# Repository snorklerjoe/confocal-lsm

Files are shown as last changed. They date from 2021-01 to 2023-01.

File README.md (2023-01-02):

# confocal-lsm
Hardware and software for my homemade **laser-scanning confocal microscope**

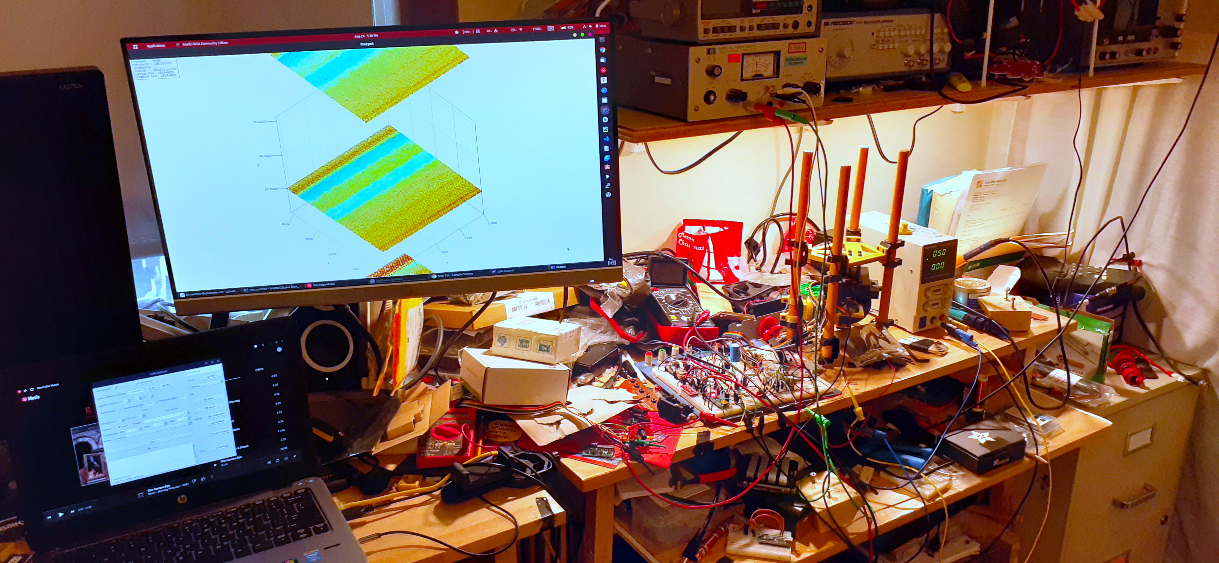
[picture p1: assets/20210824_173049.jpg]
My desk during development


_My desk during development_

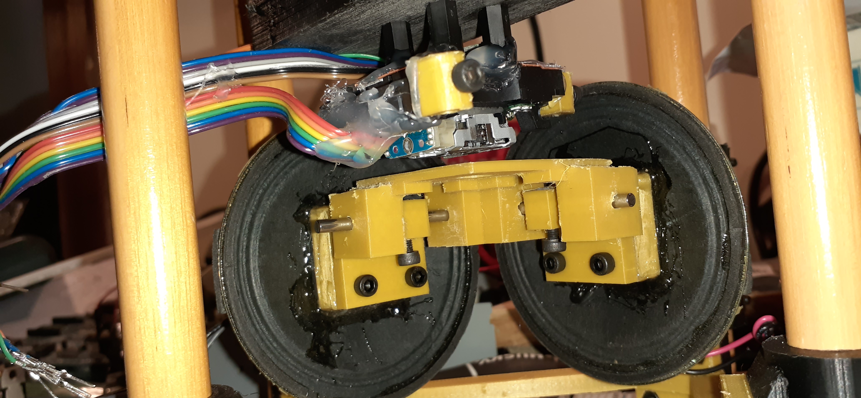
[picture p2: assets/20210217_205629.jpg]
The Scanning Mechanism


_A close-up of the scanning stage and optical head_

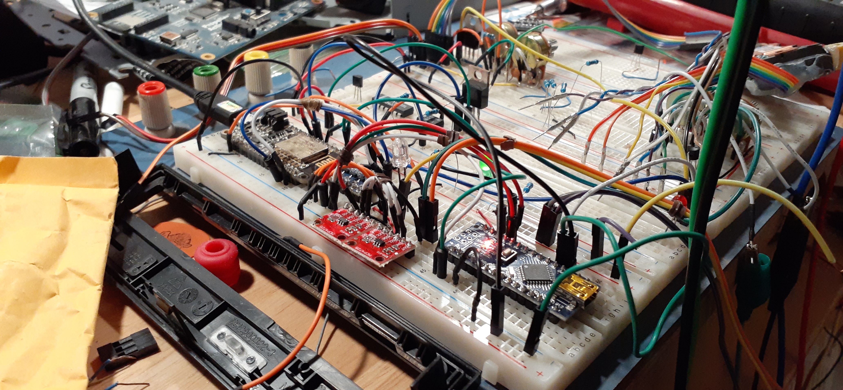
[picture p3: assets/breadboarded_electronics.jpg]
A picture of the breadboarded electronics


_Breadboarded control electronics_

## Origins...
After reading [this Instructables](https://www.instructables.com/id/Laser-Scanning-Microscope/) and [this Hackaday article](https://hackaday.com/2017/02/15/speakers-make-a-laser-scanning-microscope/),
I thought it would be interesting to try my hand at building a laser scanning microscope from CD/DVD drive parts...

# Iterative Development:

## V1 (~Summer 2018)
The first iteration scanned the specimen in the x and z axes to change its position relative to a laser beam. The diffused reflection was then measured by a usb camera and recorded into software.

This configuration was not confocal, and could only measure the X-Z plane, but was rather intended as a proof-of-concept test in which I began to learn how to explore this topic deeper.

This first "successful" scan is _most likely_ the product of the laser being brightest with the electromagnetic actuators (taken from the tracking assembly of a CD drive head) most centered (drawing the least current) due to resistance in power distribution:

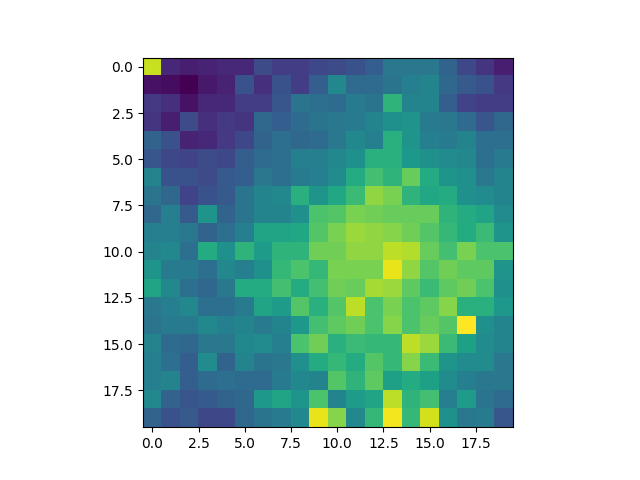
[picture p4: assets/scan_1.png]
scan 1


## V2
The second iteration was the first iteration to be confocal. I used a microscope slide as a beam splitter, with the laser going through a lens moved by the CD drive actuators and a speaker to achieve a third axis of motion. The reflected light was measured by a photoresistor, which proved to have too high of a latency for large scans to be practical.

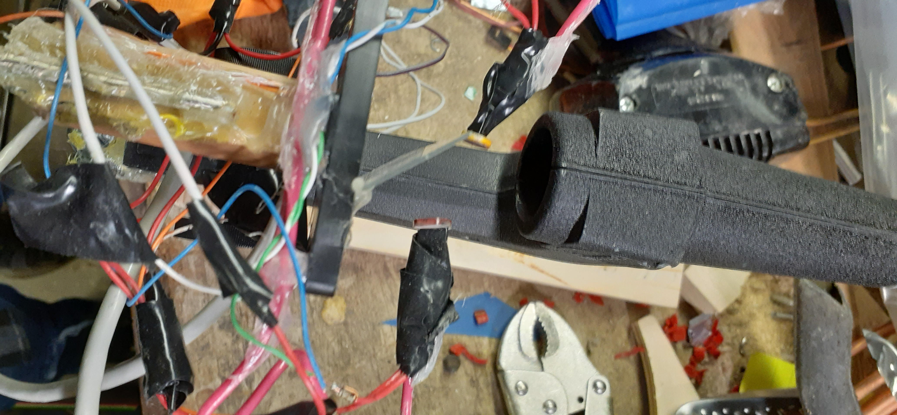
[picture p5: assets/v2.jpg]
The optical layout of prototype 2


Ultimately, due to issues of optical beam quality, the laser could not be focused to a small-enough point to be able to draw conclusions from any results of this revision.

I experimented with different lasers in this iteration in an effort to avoid this problem, using a CD laser and a laser diode from a common laser pointer.

In doing this, I also experimented with a number of simple laser driver circuits (current-limited supplies)

## V3 (2020)
The third iteration rehashed the idea of using a speaker as an actuator, but used a USB camera again as a sensor. I repurposed a desktop PC case and power supply for this iteration to provide a rigid mounting system and reduce current limitation issues.

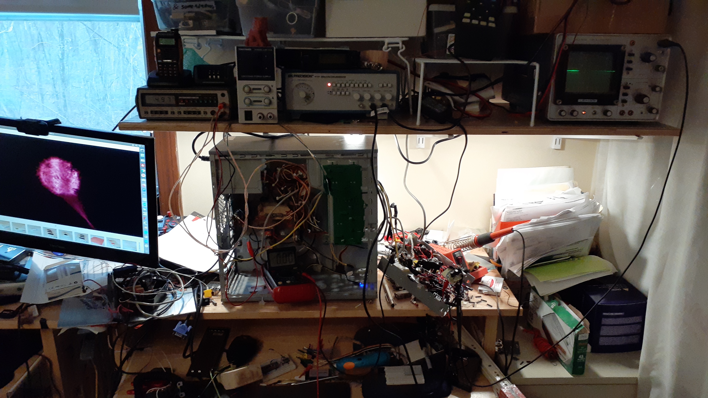
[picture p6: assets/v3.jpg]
An image of my desk with V3


_Testing for independence of laser intensity and actuator current draw (good power distribution)_

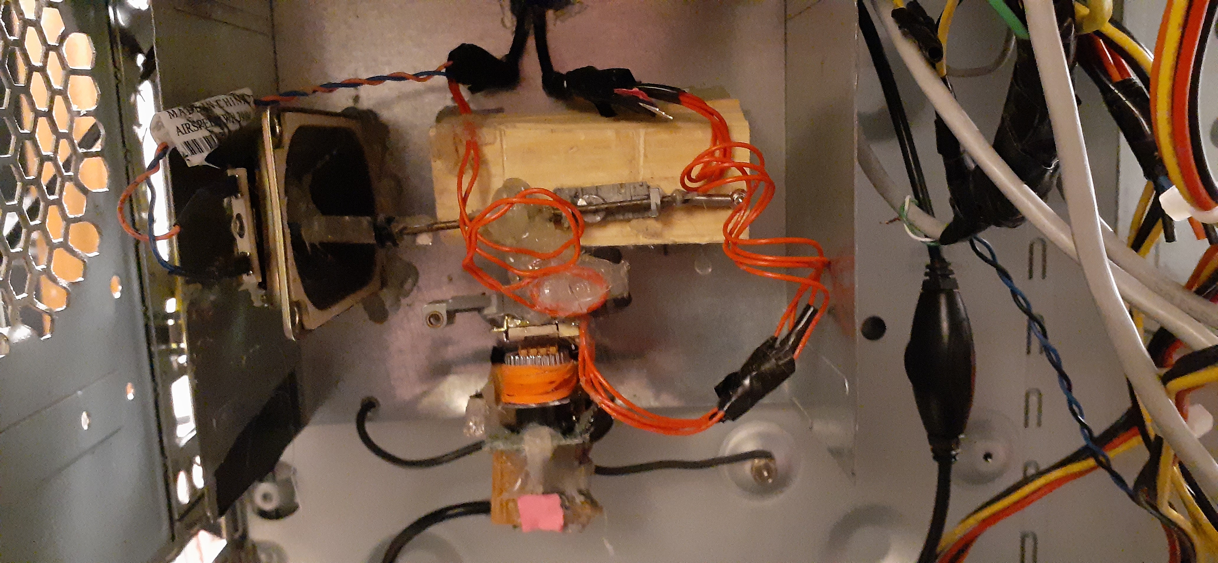
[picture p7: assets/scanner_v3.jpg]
The actuators & scanning mechanism!


_Closeup of the scanning mechamism_

This iteration also involved completely rewriting the software- I created a graphical user interface with PyQT4 and rewrote the image processing to obtain more accurate intensity measurements from the USB camera:

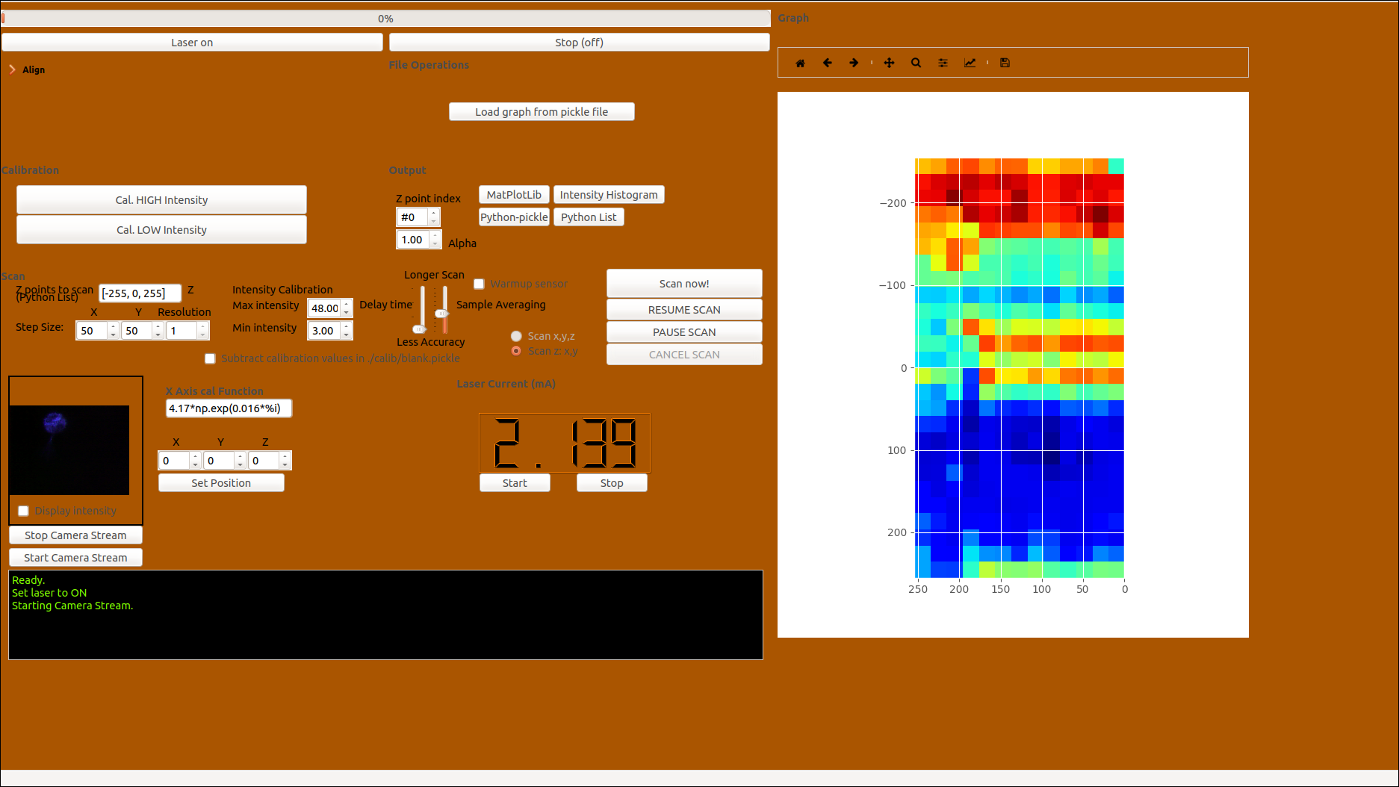
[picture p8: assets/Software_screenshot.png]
Software Screenshot


_A screenshot of the GUI_

I did manage to get a few reasonable images from this iteration of the microscope, the best one being the following:

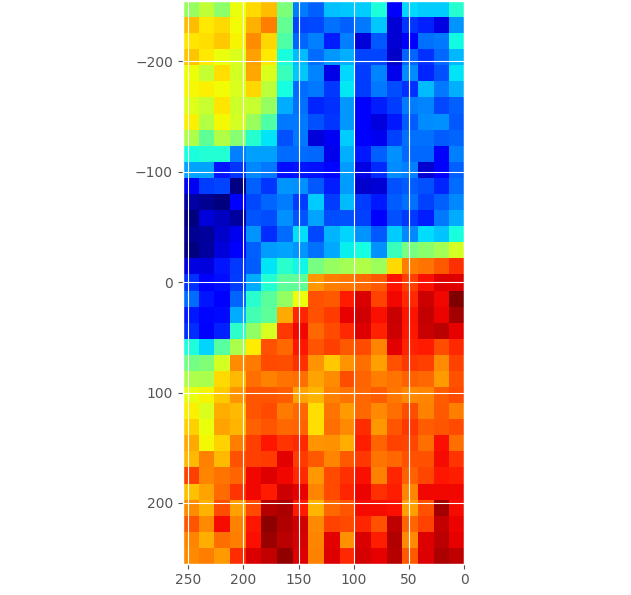
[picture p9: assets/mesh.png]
A Scan


_A scan of the mesh from a speaker grille from a handheld radio_

## V4 (2021-Current)
### Using a Photodiode...
For this iteration, I decided to further investigate how to measure the intensity of transmitted and/or reflected light.
I observed the die of a photodiode used in the optical head of the CD drive under a microscope:

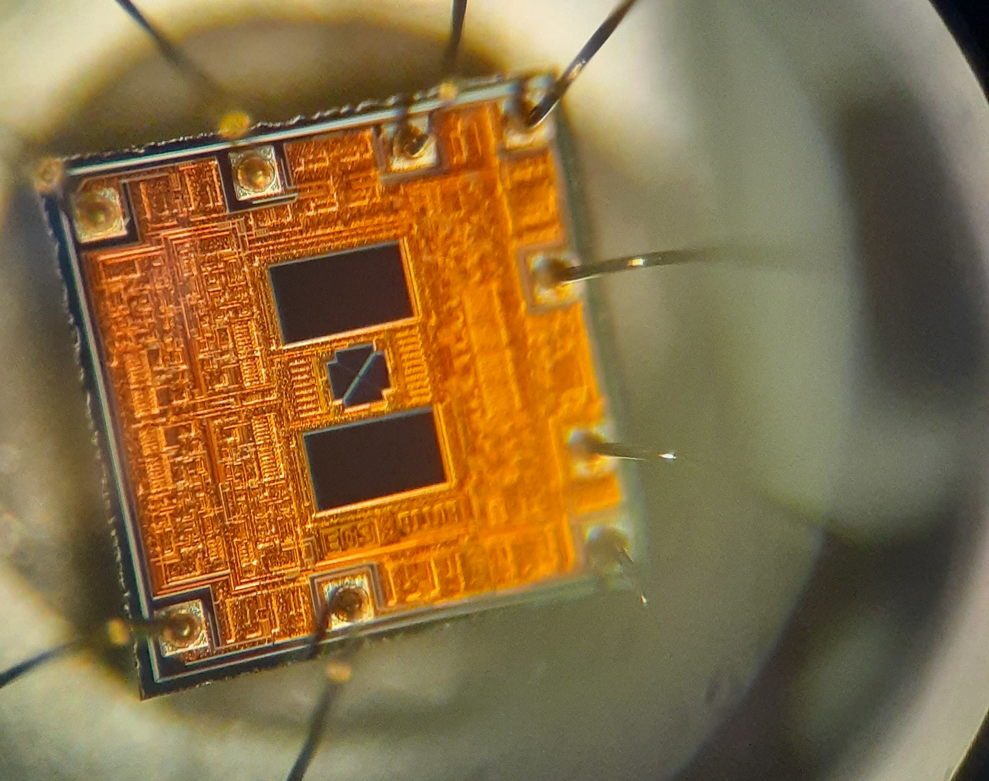
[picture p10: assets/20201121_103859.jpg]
Compound photodiode die under the microscope


It happens that CD drives use a compound photodiode to assist in focusing. After a number of attempts to interface to this photodiode as it was wired into the electronics of the CD drive, I settled upon using a different photodiode instead.

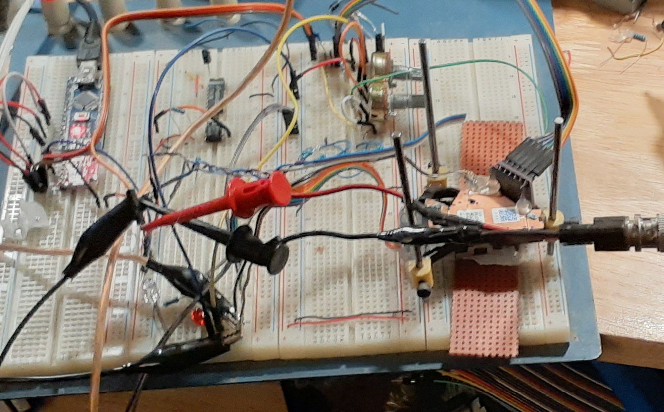
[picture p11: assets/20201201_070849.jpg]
Testing with the new photodiode


### CAD & Redesigned Scanning Mechanism

I then designed a modular frame in FreeCAD, before transfering my design to Fusion360:
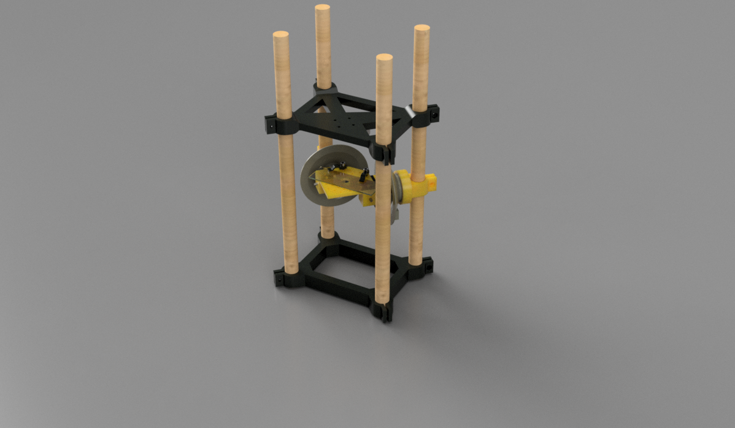
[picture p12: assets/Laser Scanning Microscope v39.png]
A 3D Render


_A Fusion360 Render of the microscope frame_

The Scanning Mechanism

_A close-up of the scanning stage and optical head_

### Electronics

There were also a number of electronic improvements in this iteration- PWM control of the actuators was replaced by 2N2222-based drivers controled by DACs. An LM317 was used to create a constant-current source for the laser diode. Also, the microscope communicates with a computer via the WiFi connection of an ESP8266, with an Arduino Nano being used to handle some of the interfacing tasks over I2C. Overall, this revision represents major improvements in reliability, resolution, and quality.

A picture of the breadboarded electronics

_The electronics on a breadboard_

### Software

The software was rewritten in Java, with a number of improvements, such as...
- Interpreted script-based description of a scanning pattern
- More flexible data aggregation
- More data processing to produce 3-D contour plots of a surface
- Threads to process and recieve data efficiently

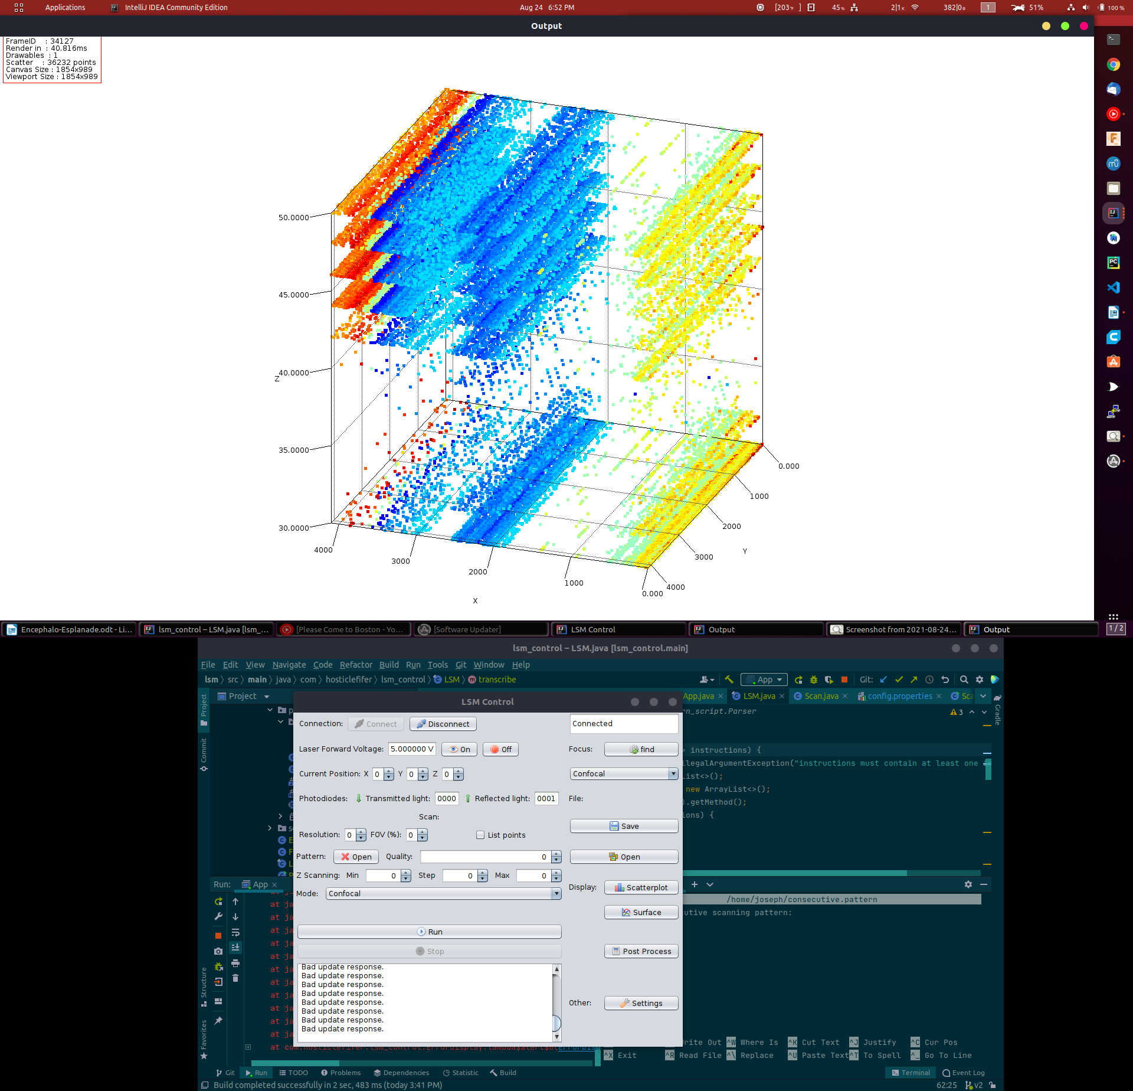
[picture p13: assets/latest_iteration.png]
A Software Screenshot


## Conclusion / Continued Work

I have yet to obtain a scan from this iteration which truly represents the specimen being scanned in an obvious and clear manner, but further work will involve reliability improvements and reducing stiction in the stage to improve precision of the actuators in order to push closer to this goal.

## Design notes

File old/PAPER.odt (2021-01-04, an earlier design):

Building a Transmission-mode Laser Scanning Microscope for Free

Joseph R. Freeston

Department of English, Windham High School

Freshman Writing

June 8, 2020

Abstract

Scientific equipment can often be produced with parts that can be found in old electronics. This paper is intended to inform about how a transmission-mode laser scanning microscope (TLSM) can be constructed for very little monetary cost. A TLSM shines a collimated laser beam into optics which focus it into a small area along the focal plane (which is on the specimen). A TLSM measures the light transmitted through an object, sometimes revealing interesting details about its structure. This reflected light is measured as the beam is scanned along the object in order to capture a grayscale image. Although most laser scanning microscopes are confocal, meaning that the light reflected off of an object goes backward through the objective lens, and is then measured, this one operates only in transmission-mode. This functional piece of equipment is capable of obtaining three-dimensional slices of almost any small, translucent object, and can be built with parts commonly found in old and broken electronics.

Keywords: arduino, laser, microscope, optics

Glossary

1. Actuator
  a. A device that actuates, or moves, something.
2. Beam waist
  a. The diameter of a beam at its focal point (Hinton, 2019).
3. Bipolar Junction Transistor (BJT)
  a. A type of transistor that allows controlling the amount of electric current going from its collector to its emitter by altering the current from its base to its emitter (See “Transistor”).
4. Cadmium-sulfide
  a. A carcinogenic material commonly found in older photoresistors (See “Photoresistor”).
5. Collimation
  a. The process of forming a beam into a straight, column-shaped one by lowering its angle of divergence.
6. Confocal
  a. Meaning that a laser will be focused onto something and in the same manner (through the same optics) be reflected backward to end up in the same place it originated from. The returning beam may also be split off into a detector at the same optical distance from the objective lens as the laser.
7. Current Source
  a. A current source is capable of maintaining a constant current output, even with varying loads, by altering its voltage output.
8. Diaphragm
  a. (In a speaker) The part of a speaker which is actuated back and forth by the coil repelling or attracting a magnet. Normally, the diaphragm turns the mechanical motion into a longitudinal wave going through the air.
9. Duty cycle
  a. The percentage of time that a pulsed signal is in the high or “on” state. If the signal remains high for 90% of the time in between spiking low, it has a 90% duty cycle (See “Pulse-width Modulation”).
10. Electromagnet
  a. A magnet relying on the magnetic field produced around a wire with current flowing through it. These are generally just a coil of wire, often wrapped around a metal core. They may be turned on and off, and even varied, electronically.
11. H-Bridge
  a. An arrangement of transistors that allow reversing the polarity of a device, such as a motor or a coil. They are commonly used to control a motor’s direction.
12. Kirchhoff's Current law
  a. A law that allows multiple devices in series to draw the same amount of current.
13. Microcontroller
  a. A small computer capable of performing calculations and controlling electronics through input/output pins (i/o pins).
14. Ohm
  a. The unit used to measure resistance to the flow of electric current, named after Georg Ohm, the man that discovered Ohm’s Law.
15. Ohm’s Law
  a. The famous equation relating current, voltage, and resistance, stating that V=IR, with “V” being the voltage drop across something, “I” being the current going through it, and “R” being the resistance in ohms (See “Ohm”).
16. Operational Amplifier (Op-Amp)
  a. A device that amplifies a signal based upon the difference between its two inputs.
17. Photodiode
  a. A device that can be used to measure the intensity of light.
18. Photoresistor
  a. Similar to a photodiode, but with a much slower reaction time. It is essentially a resistor whose resistance changes based on light intensity (See “Resistor”).
19. Power supply
  a. A device which usually supplies (a) specific voltage(s) to an electronic circuit, generally converting the high voltage alternating current from an electrical outlet into low-voltage direct current.
20. Pulse-width Modulation (PWM)
  a. A method of synthesizing a nearly analog signal from a digital one by pulsing something and adjusting the duty cycle (See “Duty Cycle”).
21. Resistor
  a. An electronic component that resists the flow of electric current.
22. Speaker
  a. A device that transforms an analog (or almost analog) electrical signal into motion, used to create sound (but used only as an actuator in this project).
23. Transistor
  a. An electronic component which acts as an electronically controlled switch, controlling the flow of electricity with another electrical signal.
24. Transmission
  a. (In the context of optics) Occurs when light goes through a transparent or translucent object.

Building a Transmission-mode Laser Scanning Microscope for Free

Laser scanning microscopy is a widely used technique for observing microscopic structures, primarily in fields such as biology. A laser scanning microscope (LSM) can generate an image by scanning a laser across a surface and then capturing the intensity of the reflected and/or transmitted light through the substance. The primary advantage that an LSM has over a generic optical microscope exists because of the way that such a microscope operates: the size of a pixel in the captured image can be as small as the beam waist of the laser used. Because of the smaller lenses and supposedly higher optical quality present, with precision equipment, an LSM can have a much higher magnification than most optical microscopes. Furthermore, LSMs allow for 3-dimensional images to be captured by taking many frames with different focal distances. Because of this, laser scanning microscopy can reveal inner structures in translucent materials, including a substance’s crystalline structure. Laser scanning microscopes are relatively simple in their construction, compared to, for example, a scanning electron microscope (SEM). Despite the common preconception that such a topic may only be explored with industrial-grade lab equipment, an LSM is not overly complicated and can be made cheaply in a home workshop.

Interestingly enough, compact disc (CD) drives operate with the same principles as confocal laser scanning microscopes. A laser is reflected off of the surface of the disc and the returning beam’s intensity is measured. According to Woodford (2019), data is stored through the lands and pits on the CD, which reflect light differently, and they can be told apart from each other by the drive. In this manner, bits of data are encoded and stored physically in an optically read medium (Woodford, 2019).

In more detail, CD drives operate in a very similar way to LSMs. The collimated laser is focused down onto the disc by the objective lens. As the disc spins, the objective lens slowly scans across it, and a separate actuator exists for focusing and tracking the laser across the disc. This optical device, capable not only of focusing a laser to a microscopic point, but also steering the beam and focusing it automatically.

LSMs have previously been constructed in the past using parts from CD drives in addition to other parts (Williams, 2017; Venkes, 2017). After noticing this, I decided to build my own with an additional challenge: that no money would be spent on the project.

Prototypes and Revisions

Project Overview

I built this TLSM in over two years, although spread throughout this timeframe were three separate prototypes (and other projects). Some parts were reused across the prototypes, but each prototype had a unique method of operation. Due to effects of experimentation, three CD drives were required, but in replicating this project, only one would be required. Each prototype also had several different parts that were improved over its life (See Appendix A).

Prototype One

The first prototype had the primary purpose of a test: I wanted to see how feasible this project would be. The overall configuration was not confocal, nor was it transmission-mode. It had a cardboard enclosure, and a screw-driven focus mechanism made from an old bolt. The laser pointed down an aluminum rod, upon which was also the lens moving assembly from a CD drive. This allowed for a single line to be scanned, one pixel by 511 pixels, at any of 511 potential focal points. Instead of having a lens on the lens moving assembly, the specimen was moved directly instead of moving the beam’s position. The non-confocal reflected light was measured by a poor quality webcam, which attempted to measure the reflected beam’s intensity. To control the (specimen) lens-moving assembly, I used an H-bridge four-channel motor controller combined with a Trinket M0 microcontroller, which emulated a mouse to communicate with the computer and scanned the laser on its own.

Prototype Two

The second prototype consisted of the frame from an old optical microscope connected to a few metal boxes with wood. The laser was held on the optical microscope frame, where it shone into a beam splitter made from an old microscope slide at a 45-degree angle. Half of the beam was then split to the first cadmium-sulfide photoresistor, and the other half went forward into a metal box. Inside the metal box was the lens moving mechanism, using the same lens moving apparatus for the Y and Z-axis, and using a speaker for the x axis. This speaker was driven by a circuit to filter a pulse-width modulation (PWM) signal so that the deflection of the speaker’s diaphragm could be accurately controlled. The diaphragm was connected to a rod that (through linear bearings) pushed and pulled the entire lens moving piece back and forth. The lens moving piece controlled the y and z axis, while the speaker controlled the x axis. The laser was intended to shine through the lens (from which it could be redirected as well) and onto the specimen. The reflected light then went back through the objective lens to the beam splitter, where half of it went back into the laser, and half of it met another photoresistor. The intended operation of this prototype was confocal, however, it did not work properly for multiple reasons.

Its primary reason for failure was the fact that the laser was too dim to be received by the measuring photoresistor. In addition to the losses from the beam splitter and lens, for confocal operation to be ideal, the specimen must be perpendicular to the laser, and the sensors (photoresistors) must be aligned perfectly (which was tricky). Despite much experimentation, the signal received of the confocally reflected light was very little compared to the tiny amount of ambient light of the room, which was dark. Because of this, the scan measured the amount of light leakage throughout the scan, which was usually the brightness of the sunlight.

Figure 1

A Photograph of the Back of the Second Prototype

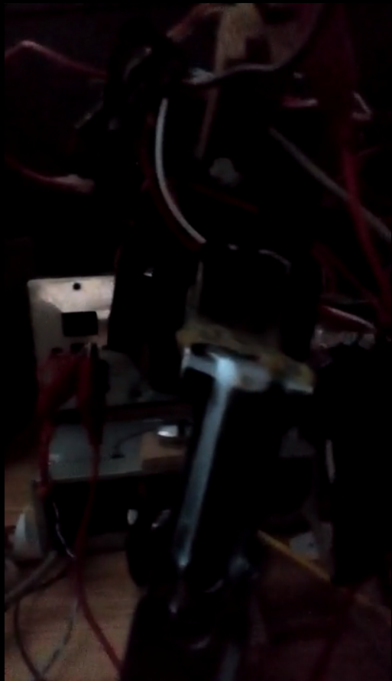
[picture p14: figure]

Another reason for the second prototype’s failure was that the beam quality present was unsatisfactory. Although it is sometimes taught that a convex lens can focus light to an infinitely small point (its focal point), this is very far from being true. According to Hinton (2019), a convex optical lens, depending on its quality, may focus a beam to have a finite cross-sectional area at its focal point, where the beam’s diameter at this point is its beam waist. Also, the smallest achievable beam waist (which produces a better resolution from the microscope) is related to the laser’s beam quality (Hinton, 2019). Beam quality is a ratio that measures this property of a beam. Higher beam qualities, depending on the method by which they are measured, often indicate a beam that is more similar to a gaussian beam, which a theoretically ideal laser beam is (Hinton, 2019). Beam quality appears to decrease as the beam propagates further, as well as from poor-quality lenses and other optical components. Due to the poor-quality laser pointer that was used, combined with impurities in the microscope slide and objective lens, and the large distance (about 16 inches) that the laser traveled because of its focal distance, the beam quality was extremely poor. This resulted in a limitation to the size of the beam waist at the specimen, meaning that the minimum pixel size for a clear scan was increased to nearly a quarter of the area it was capable of scanning. For these reasons, the second prototype served primarily as a learning experience, teaching me the skills necessary for building a third, and working, prototype.

Prototype Three

The third, and current, prototype consists of the same lens moving assembly from the second prototype, modified so that the entire laser module from a CD drive slides along the X-axis. This shines a beam directly onto the specimen (focused by the objective lens built-in to the laser module). The light that is transmitted through the specimen is focused into the optical sensor from a cheap USB webcam. As the laser is scanned across the specimen, the transmitted light’s intensity is measured through image processing and stored for display on a graph by a computer. The microscope is also housed within the case from an old personal computer (PC). Beam quality is acceptable, as the laser used should be capable of being focused small enough to read a CD, and general operation works well. A picture of this prototype is shown in Figure 2.

Figure 2

Prototype Three

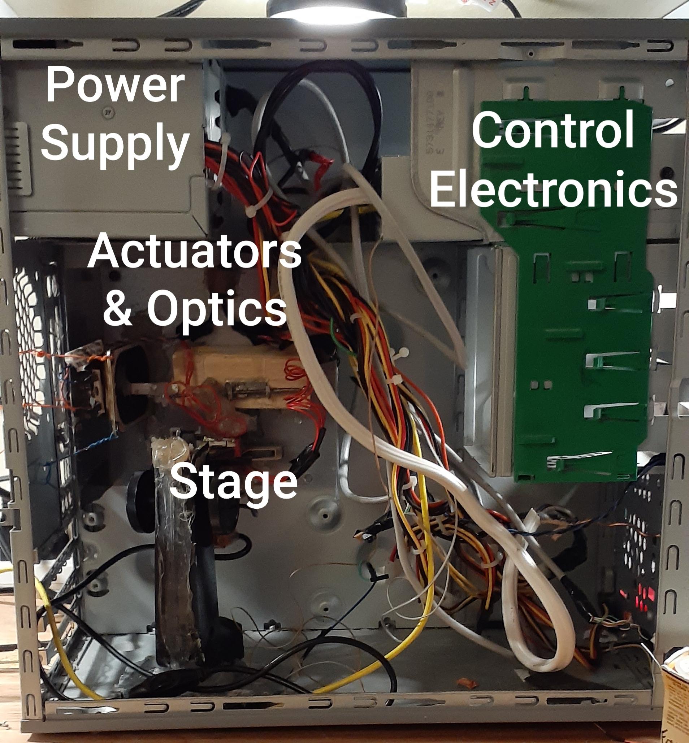
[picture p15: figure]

Note. The control electronics are housed within the case of a CD drive, the insides of which may be seen in Figure 4.

Theory of Operation and Usage

The microscope operates by scanning a focused laser beam in the X, Y, and Z directions across a translucent object. The transmitted light’s intensity is measured by a USB camera and put into an image with software, with each location measured by the laser representing a pixel. The electronics are easily explained by examining the schematic in Appendix B. Usage is demonstrated, in addition to an explanation of the microscope, in the following video: 20200604_213744.mp4 (https://drive.google.com/file/d/1Vu4TNR902r6aQBeG_PnGs2aCM6A9X-Mp/view?usp=sharing).

Software

The software, written in Python, is operated through a graphical user interface (GUI) that I made with QT Designer. When a scan is initiated with a step size and a list of focus levels to use, the software initializes and begins the scan automatically. The laser is controlled and scanned across the specimen by sending commands to the Arduino Nano microcontroller acting as the interface between software and hardware. The transmitted laser’s intensity is measured by a USB camera. An image is taken and averaged to get the overall brightness, and essentially the intensity of the laser. Each of these values becomes a pixel. A screenshot of the software is given in Figure 3. A copy of the software is uploaded to https://drive.google.com/drive/folders/1klmBxgbNrT-C8QPAXFWqk-q2L1XAimAe?usp=sharing.

Figure 3

Screenshot of the Software GUI

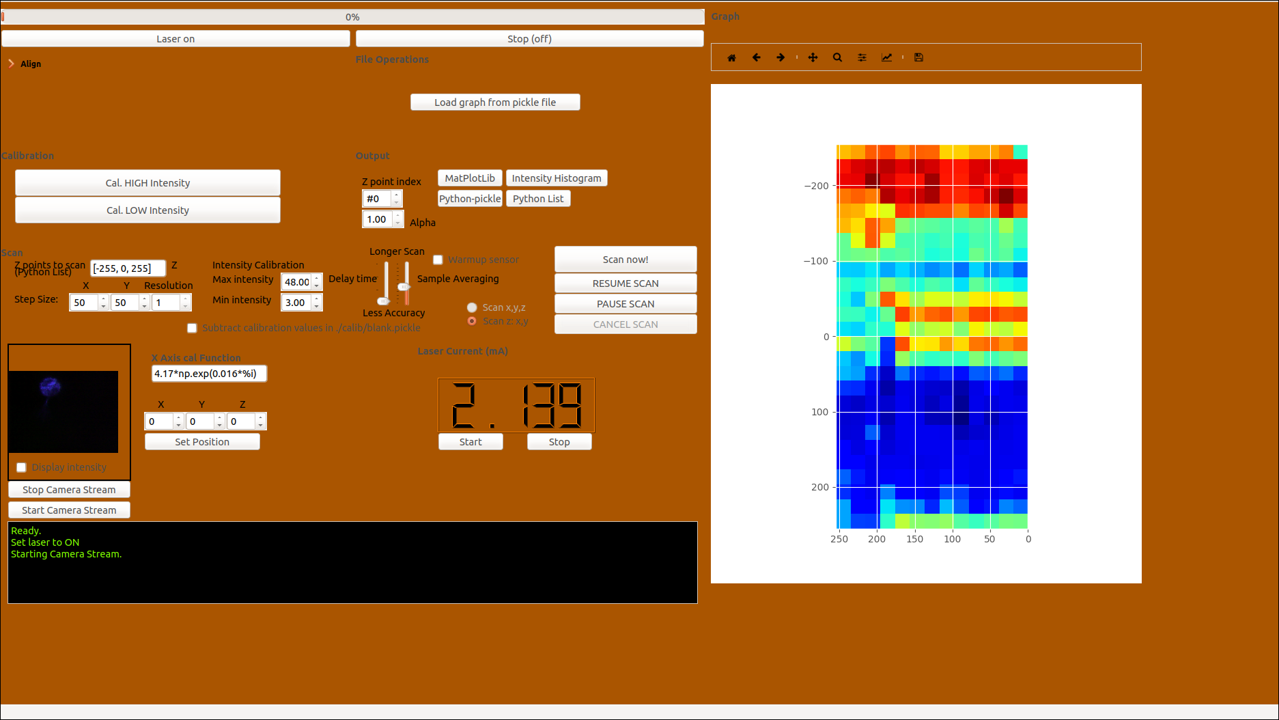
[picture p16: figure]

Hardware

Optics. The optical system of the microscope is relatively straightforward. It consists of a laser diode whose light is collimated (forced into a straight beam) and reflected downwards and into the objective lens. The moveable objective lens focuses the laser through the specimen and into another lens, which focuses the transmitted light into the image sensor of a USB webcam.

Electronics. The electrical system of the microscope is best defined and explained with the schematic in Appendix B. A picture of the electronics is displayed in Figure 4.

Figure 4

A Photograph of the Inside of the Control Electronics Box

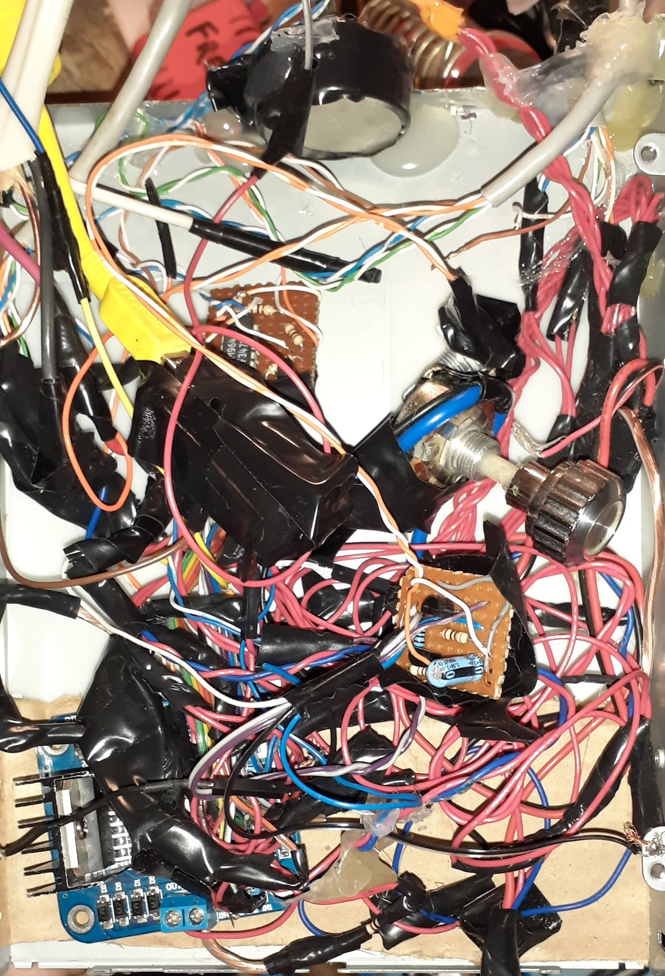
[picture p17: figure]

Safety

Safety precautions that should be taken while operating such a contraption are also important to note. The laser diodes found in laser pointers, such as the one used in the first two prototypes of this project, are generally Class II lasers. These are considered safe for “normal use,” while staring at them may still cause eye damage (“Laser Safety Facts”, 2013). The laser diodes found in CD players are Class 3R and Class 3B lasers. These can cause eye damage, and stronger Class 3B lasers can potentially cause fire and burns when focused (Kobrle, n.d.; “Laser Safety Facts”, 2013).

The laser in the third and current prototype of the TLSM has a very close focal distance (a few millimeters, depending on adjustment), and uses a generally low power. Because of this, the intensity of laser radiation is too small to do damage by the time it has passed through the specimen, and the laser (given very little power) is very safe.

The initial prototypes presented a much higher risk, as the laser, although of a lower class, was being driven with more power. There were also exposed lenses, which could have acted as partial mirrors and reflected part of the laser towards someone’s eyes. For this reason, great care must be taken when handling and operating almost any lasers.

Results

Though initial results were vague and sometimes quite poor, later results became increasingly better. Merely the vague outline of things was visible from earlier scans, and with incremental improvements, the captured images have become clearer.

While the microscope is theoretically capable of taking a 256 by 511-pixel image, each pixel being an estimated 17 microns across diagonally, lower-resolution scans have yielded far greater success. The greatest success has been observed in images with a step size of 20 (skipping all but every 20th pixel, basically), or a resolution of 12x25. Higher resolutions can be achieved, although to maintain accuracy, these can take upwards of 10 hours. Scans with resolutions higher than 15x34 tend to have issues regarding the X-axis’ movement being inconsistent, likely due to the small step size and potentially due to heat. This could likely be fixed by placing a small fan near the speaker which drives the X-axis, and/or increasing the delay between pixel measurements. Nonetheless, the clarity of the images produced by the TLSM is not hampered by low-resolution scans. Although many scans use a low resolution, they are only scanning an area somewhat smaller than the size of the cross-section of a pencil. Observing this, as well as the estimated minimum pixel size of 17 microns, the TLSM may be useful as a tool and piece of equipment. It can obtain three-dimensional slices of the inner structure of a translucent object and see what cannot be seen with the naked eye, therefore accomplishing its goal.

Figures 5-7 show a few of the best scans. The speaker grille from a cheap Baofeng handheld radio is shown in Figure 5. The cells of the mesh (the red/yellow areas) are approximately 60 mils (thousandths of an inch) across, and the wire in the mesh (the blue) has a diameter of 20 mils. Figure 7 shows a piece of plant lice, with one of its legs visible, and Figure 8 is of a slide with some bean starch on it. Towards the middle-left of Figure 8, a near individual grain is visible.

Figure 5

A Scan of a Cell of the Speaker Grille from a Handheld Radio

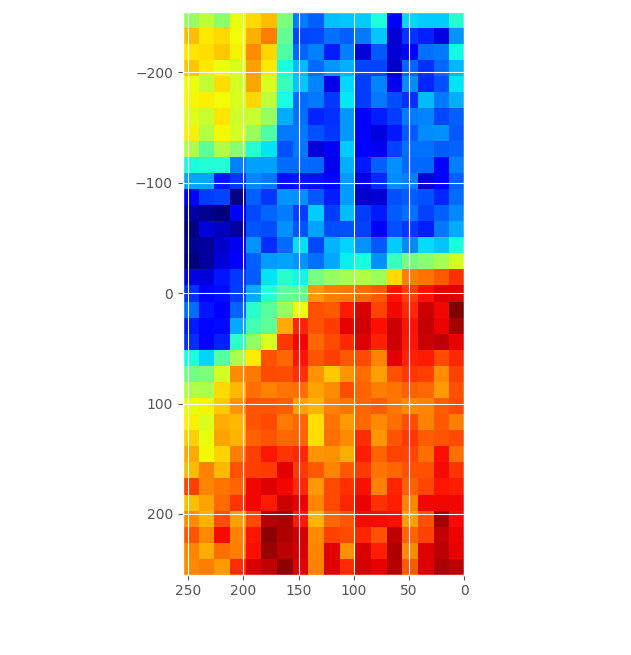
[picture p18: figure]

Note. Blue areas indicate low transparency, with red indicating the opposite. The yellow and red regions of the image are cells of the mesh.

Figure 6

A Scan Displaying Part of a Piece of Plant Lice

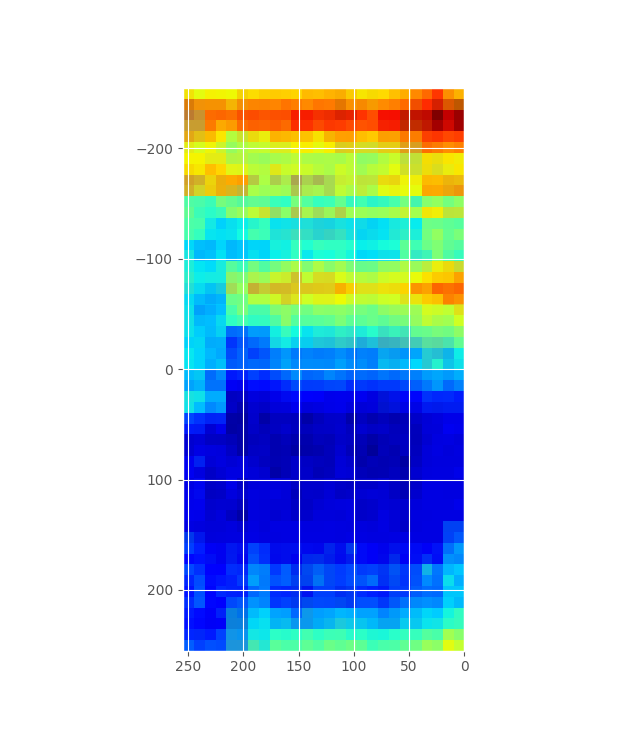
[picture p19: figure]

Figure 7

A Scan of Bean Starch

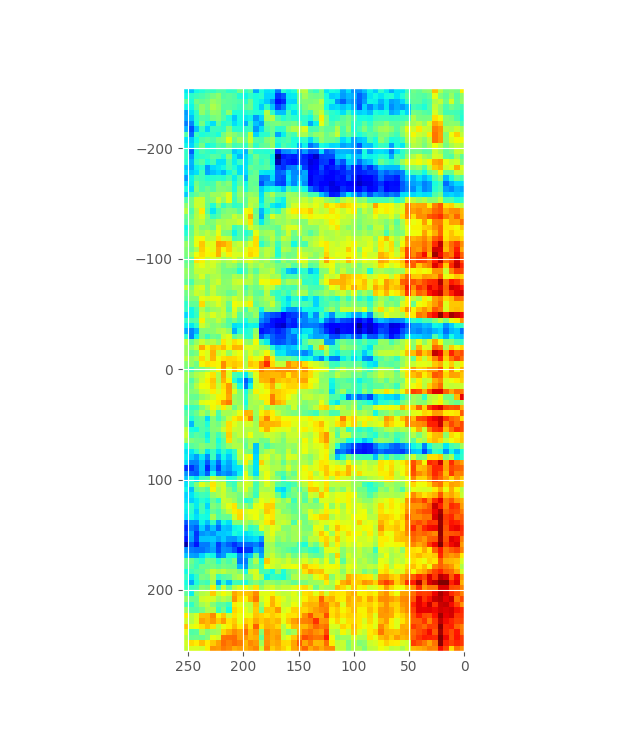
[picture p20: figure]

In conclusion, the microscope fulfills its purpose, and could even be used as equipment for help with other projects involving microscopic details. The effort that I put into it was well worth my time, and I may even continue to make it better. It will likely never have the same quality that some commercial industrial laser scanning microscopes offer, but it is a functional microscope, and hence achieves its goal.

References

Arduino. (2008). Arduino Nano (V2.3). Arduino - Home. https://www.arduino.cc/en/uploads/Main/ArduinoNanoManual23.pdf

(Arduino Nano Datasheet)

Bigelow, K. (n.d.). The basic current mirror. Play-Hookey. https://www.play-hookey.com/analog/current_mirrors/current_mirror_basic.html

Hinton, R. (2019, June 1). Beam propagation and quality factors: A primer. Laser Focus World. https://www.laserfocusworld.com/lasers-sources/article/14036821/beam-propagation-and-quality-factors-a-primer

Laser Safety Facts. (2013, November 23). https://www.lasersafetyfacts.com/

Jameco Electronics. (n.d.). Muscle wire FAQ. Jameco Electronics - Electronic Components Distributor. https://www.jameco.com/Jameco/robot/muscleqa.html

Keim, R. (2016, April 11). Low-pass filter a PWM signal into an analog voltage - Technical articles. All About Circuits - Electrical Engineering & Electronics Community. https://www.allaboutcircuits.com/technical-articles/low-pass-filter-a-pwm-signal-into-an-analog-voltage/

Kobrle, D. (n.d.). Laser diodes from CD-RW drives can cut and burn! DANYK.CZ - Elektrotechnika, shémata, návody. https://danyk.cz/laser_en.html

Koheron. (2018, October 16). Understanding the basics of laser diode drivers. https://www.koheron.com/blog/2018/10/16/understanding-the-basics-of-laser-diode-drivers

Venkes. (2017, February 5). Laser scanning microscope. Instructables. https://www.instructables.com/id/Laser-Scanning-Microscope/

Williams, A. (2017, February 15). Speakers make a LASER scanning microscope. Hackaday. https://hackaday.com/2017/02/15/speakers-make-a-laser-scanning-microscope/

Woodford, C. (2019, August 30). How do CD and DVD players work? Explain that Stuff. https://www.explainthatstuff.com/cdplayers.html

Appendix A

Hardware Revisions

Many revisions and iterations of nearly every part of the microscope have been made as features have improved. Later, subsequent iterations are generally either simplified or more advanced versions of a previous version of a part, depending on its use.

The Laser and its Driver

Given that, seemingly, the most important part of the microscope is the laser, it and its driver have a large impact on the success of the entire project. The laser, in the first two prototypes, was a simple diode laser that can be found in almost any handheld laser pointer. No driver was used. This laser had a poor beam quality, and also dimmed and brightened almost spontaneously upon changes in the current load on the power supply (which is also indicative of the power supply being somewhat overloaded). In the last prototype, a higher-quality diode laser from a CD drive was used, along with the collimating and focusing optics and the lens moving mechanism from one. Laser diodes must be used with care, not only for safety purposes, but to increase their longevity. Applying direct voltage can ruin a laser diode, as they have very little “forward resistance,” and they may easily be burned out (Kobrle, n.d.). The current going into a laser diode must be kept constant to ensure that its optical output is consistent. This is because laser diodes produce heat when on. As they heat, their resistance changes, meaning that more or less current will flow through them and their intensity will vary (Koheron, 2018). This must also be avoided.

In its simplest form, a laser diode driver is nothing but a current source. Although expensive industrial laser drivers can monitor (using the photodiode that is built in to many laser diodes) the laser’s output power and aim to keep that consistent, the one used here only monitors current.
The first revision used a current mirror, a device which uses bipolar junction transistors (BJTs) to mirror the current going through one device (usually a resistor) through another device. A current source can be made by having a fixed resistor with a “reference current” across it, and have the same amount of current be mirrored across a device (Bigelow, n.d.). Although this worked very well as an accurate current source, when the load (the laser) was disconnected, the transistors overheated in an attempt to push more current through the open load by increasing their base current to several milliamps. Because of this, combined with experimentation, a current mirror proved to be a poor choice for a laser diode driver.

Figure A1

One of the First Laser Driver Prototypes, Using a Current Mirror

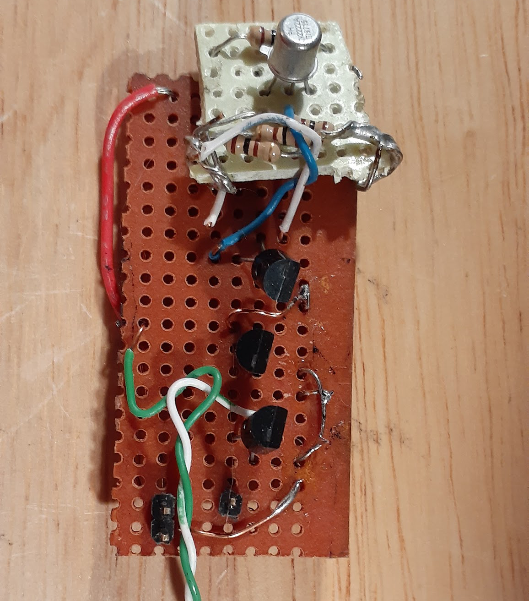
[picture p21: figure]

The second attempt repeated the first, but with a heatsink on the transistors to make them overheat less easily. This, for the same reason, failed, and I moved on to another idea. The circuit may well have worked with higher-power transistors, such as 2N2222a transistors, but this was never tested.

The third, and current, laser driver is a current source operating as follows: Current flows from the collector of an NPN BJT to its emitter, and then through the load (again, the laser diode). Current then flows through a resistor to ground. The resistor is current-limiting, as well as to separate the node between it and the load from ground (and, to some extent, acting as a current-sense resistor as well). An operational amplifier measures between power and the top of the resistor, and outputs this difference to the base of the transistor, forming a feedback loop which attempts to keep the voltage at the cathode of the laser diode constant. This keeps the current through the resistor constant due to Ohm’s law, and, because of Kirchhoff's Current Law, the current through the laser diode is the same.

Figure A2

Current Laser Driver

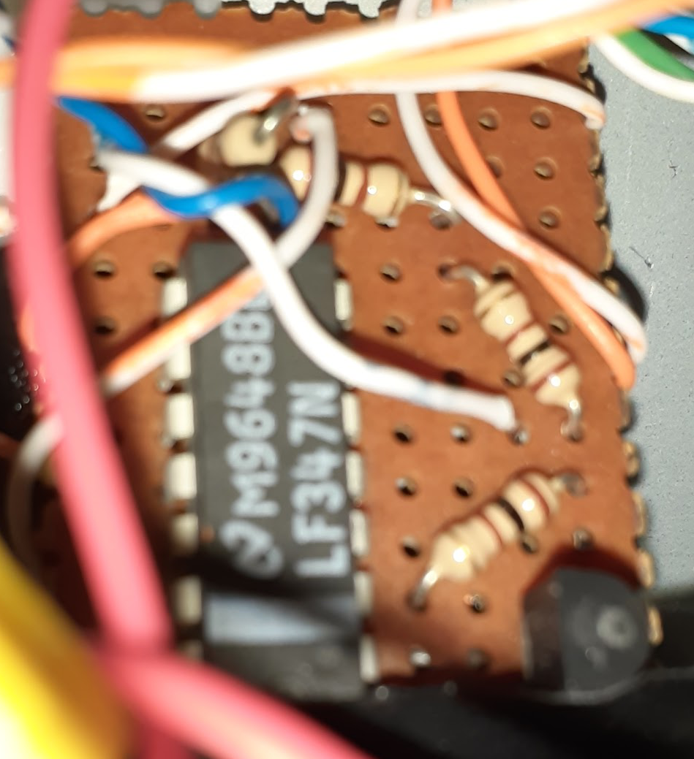
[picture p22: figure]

Lens Movement

The laser can scan because of the movement of the objective lens that directs it. In the first two prototypes, the same mechanism was used as that which is used in a CD drive to move the lens, although the third prototype includes the entire CD read/write head from a drive. This read/write head includes optics (to collimate the beam, reflect it downwards, and focus it), as well as a laser and lens-moving mechanism for the objective lens. This lens-moving mechanism is relatively simple: an objective lens with coils on each side of it is suspended in a cavity by its coils’ power wires. These coils act as electromagnets, producing a magnetic field when energized. These push/pull against the fixed magnets on the sides of the cavity, allowing the objective lens to move up and down (focus) as well as back and forth. The other axis is normally taken care of by the spinning of the disc.

Figure A3

A Lens Moving Mechanism

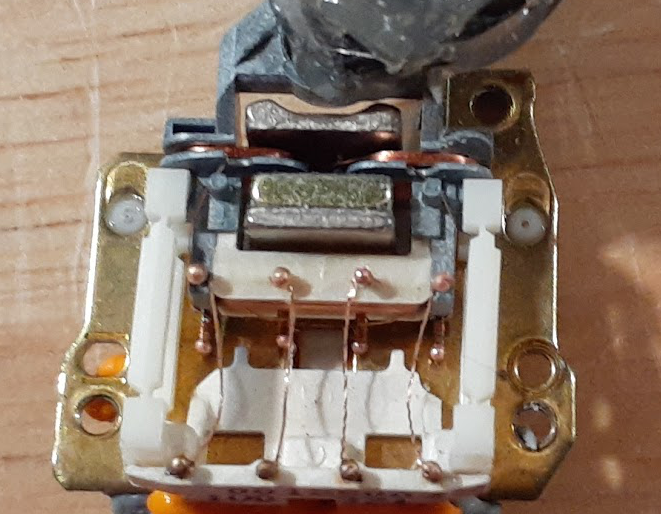
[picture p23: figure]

Note. This lens moving mechanism operates slightly differently from what is described because the one in the microscope is difficult to take a picture of and this one is unconventional.

In the second and third prototypes, a 1.5 watt, 8 ohm speaker was used to move the laser for its X-axis. To utilize the speaker as a precise actuator, a PWM signal is smoothed and averaged by a circuit that charges and discharges a capacitor, creating an analog output which is used to drive the speaker. A simple digital to analog converter (DAC) can be made in this manner, by filtering and smoothing the PWM signal (Keim, 2016). By adjusting the duty cycle of the PWM signal, the speaker can be moved back and forth. Unfortunately, the relationship between the duty cycle in and the current out across the speaker is logarithmic instead of linear, which would be ideal. This is because of the circuit that drives the speaker. To correct for this nonlinearity, the inverse of this logarithmic function (which is an exponential function) is used in the software to counteract it. Without correction, the captured image is stretched in its X-axis according to a logarithmic function, which makes it difficult to interpret.

I did experiment and think about alternatives to a speaker for the X-axis movement, however, the speaker appeared to accomplish the task in the best manner possible. I considered using muscle wire, a type of resistive wire which expands and contracts with heat, and, therefore, with current (Jameco Electronics, n.d.). It appeared as though it would be difficult to control with fine movements such as the ones that were needed. I also experimented with using a micro servo to actuate a lever arm slightly off-center from the axis of rotation, but that could not have produced the same potential resolution. Because of the factors limiting the alternatives, I settled on utilizing a speaker for the X-axis movement.

Figure A4

Speaker Driver, First Revision

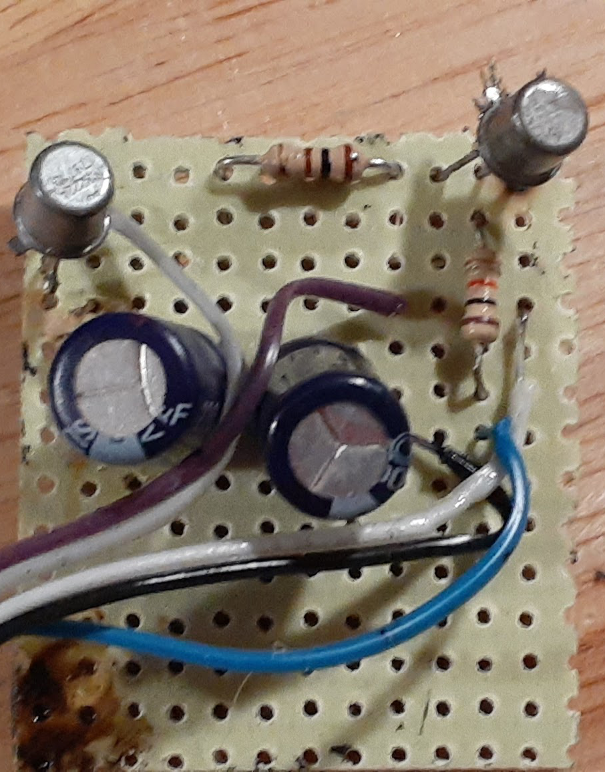
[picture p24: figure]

Figure A5

Speaker Driver, Second Revision

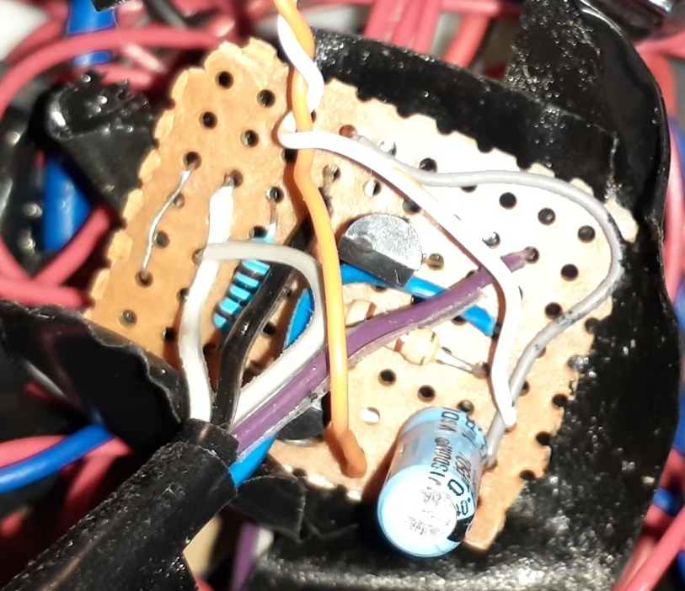
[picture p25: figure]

Detector

Once the laser is aimed through or at an object, the transmitted (or reflected) intensity of the laser must be measured. This was done initially with a Universal Serial Bus (USB) camera. This camera had issues with brightness correction mid-scan, removing a lot of consistency. The second prototype used photoresistors to measure the intensity of the laser before and after reflecting off of the specimen. These were highly susceptible to shifts in ambient lighting conditions, and were not sensitive enough to effectively measure the reflected laser off of an object other than a mirror. The third prototype employs a slightly higher-quality USB camera for a detector, which appears to have worked very well. Intensity is measured out of the camera simply by averaging together each of the channels of all of the pixels in the image to obtain the overall brightness. If the only thing visible in the image is the laser, this will calculate the laser’s brightness at that point.

Controller

The first microscope utilized an Adafruit Trinket M0 microcontroller to provide an interface between the computer software and the hardware. Due to its lacking number of input/output (i/o) pins, it was later replaced by an Arduino Nano microcontroller in the second and third prototypes. The Arduino Nano has eight analog inputs and 14 digital i/o pins (Arduino, 2008). These are useful for monitoring levels and getting input from photoresistors and other analog sensors, and for controlling many aspects of the microscope’s operation. Another advantage of this microcontroller is its support and documentation, as the Arduino has become a standard microcontroller platform for hobbyists around the world, as is clear through their website, https://www.arduino.cc.

Appendix B

Full Electrical Schematic of the Microscope

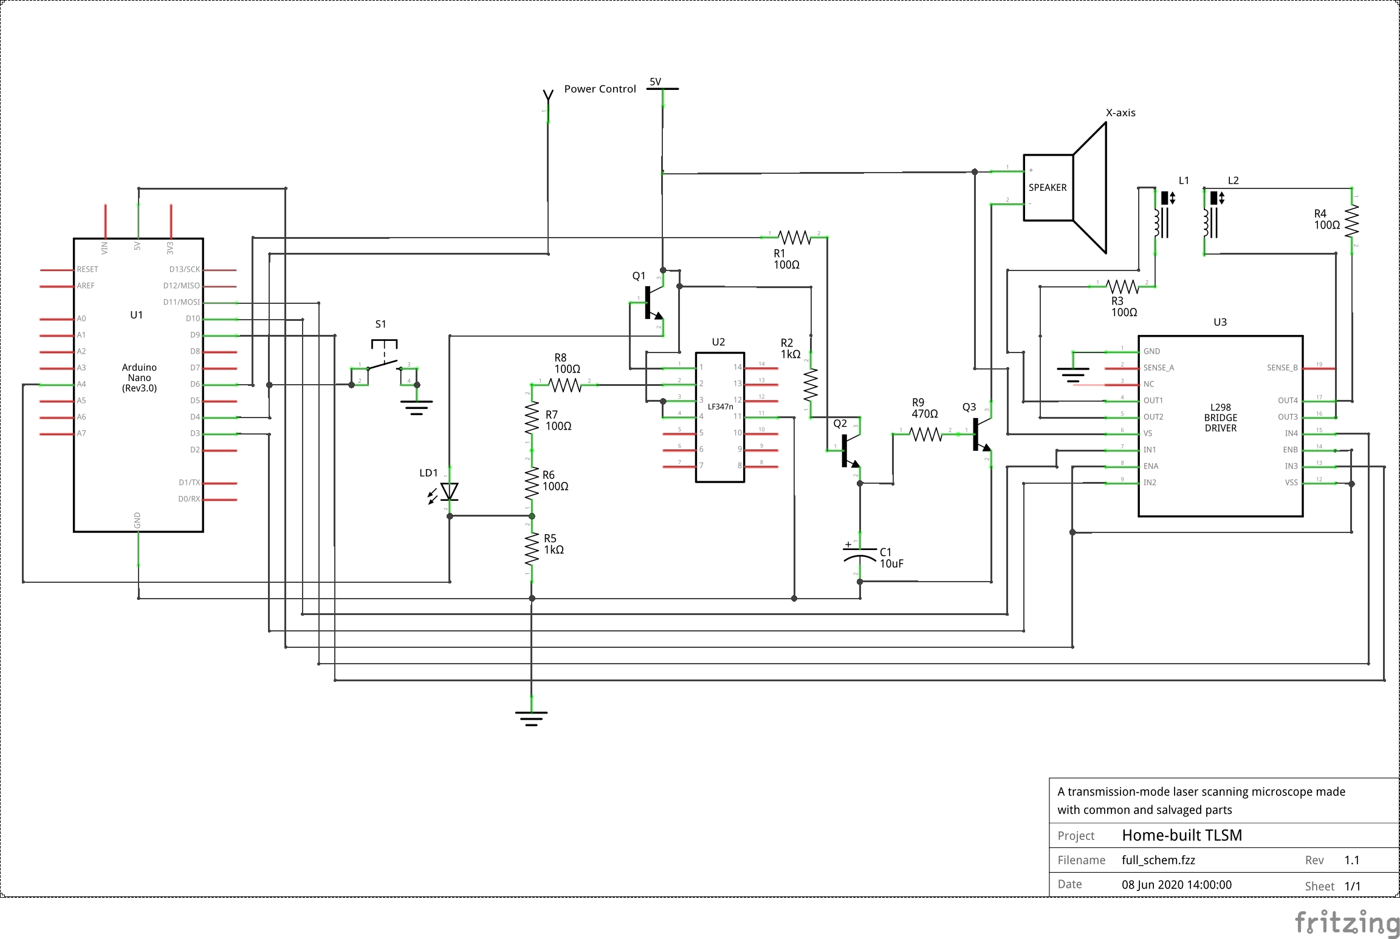
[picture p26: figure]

The Arduino Nano, U1, receives commands via USB from the software running on a computer. These commands allow it to turn on/off the laser and lens movement by pulling pin D4 low, providing a path between the (ATX) power supply control pin and ground and powering up the supply. Commands can also send the focused laser point to a specific (x,y,z) location by pulse-width modulating pins D3, D6, D9, D10, and D11 to control the speaker driver and H-bridge circuit.

The X-axis is moved to a specific location by pulse-width modulating pin D6. This turns transistor Q2 on and off, charging C1, which drains into Q3 through R9. This acts as a buffer, averaging the PWM signal to prevent the speaker from sounding too loud of a tone from the PWM. Q3 drives the speaker based on the current through R9 (due to Kirchhoff's Current Law), which is dependent on the voltage across C1, which is dependent on the duty cycle of the PWM signal which charges it. To keep the voltage across C1 at a relatively constant level, the capacitor is also constantly drained through R9 and Q3.

The laser is driven by a simple current source. U2, an Operational Amplifier, and Q1, along with the surrounding resistors form a feedback loop attempting to keep the voltage at the cathode of the laser diode constant (Koheron, 2018). The current across the laser diode LD1 is equal to the current across R5, because of Kirchhoff's Current Law and the fact that Operational Amplifiers (including this one) have high input impedances (As can be found in their datasheets). Because of this, the current across LD1 can be found by measuring the voltage at its cathode (which is the voltage across the resistor R5) and utilizing Ohm’s Law. By this method, the software (through the Arduino) can measure the current across the laser, which is a useful thing to know.

The Y/Z movement is accomplished with U3, a cheap L298 H-Bridge motor driver board to double the range. Because of this, the image is always at a 1:2 aspect ratio.

Appendix C

Parts used

I used many supplies and parts in this project through each iteration of each part. The following is a list of the parts and materials required to build the final prototype.

- An old computer case
- A computer power supply
- The case from a second computer power supply
- At least one CD drive
- CAT-5 wire (could be almost any wire of at least that thickness)
- Some other, bigger wire
- Female crimp-on connectors for connecting to the Arduino
- Arduino nano
- An assortment of resistors (See Appendix B)
- At least 3 2N2222A NPN transistors
- A momentary switch
- An LF347N quad op-amp chip (or a similar op-amp)
- A 10 μF capacitor
- A 1.5 or 2-watt speaker
- An L298 motor driver module
- USB to Mini USB cable
- USB webcam
- Some scrap wood
- Hot glue
- An assortment of fasteners and screws
- Rosin core lead solder
- Electrical tape
- Perf board or solder breadboard

Tools/Equipment Used

The following tools were used in the making of this project. They are not all necessary, but many of them facilitate the building process and make it much easier.

- Some sort of calipers or a micrometer
- Crimper
- Wire strippers
- Needle-nose pliers
- Vice-grips (locking pliers)
- Vice
- Some clamps
- Hacksaw
- Metal shears
- Handsaw
- Soldering pencil
- File
- Screwdrivers
- 2 Mhz Function generator
- Oscilloscope (x2)
- Digital multimeter (x2)
- Benchtop power supply
- Alligator clip leads (x5 at least)

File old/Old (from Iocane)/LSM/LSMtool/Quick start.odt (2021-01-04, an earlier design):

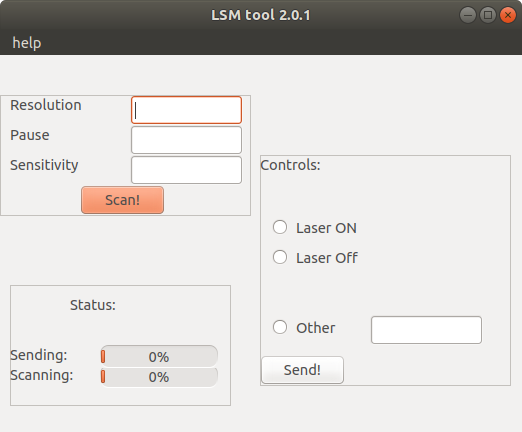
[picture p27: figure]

Progress bars

LSM controls

Scan controls

Help menu

Scan button!

Using LSM tool 2.0.1 is a piece of cake! All you need to do is type in the following details and hit Scan!

- Resolution
  - This is the control for the scan resolution, but it is kind of backwards!
    - It is the number of the percent of the range of the microscope of “possible pixels” to skip, between 0 and 100, a larger value indicating a lower resolution, and a shorter scan time.
  - Keep in mind that this value is out of the 200 pixels in BOTH the X and Y directions.
- Pause
  - This is the number of “centiseconds” (seconds divided by one hundred) to wait in between each pixel.

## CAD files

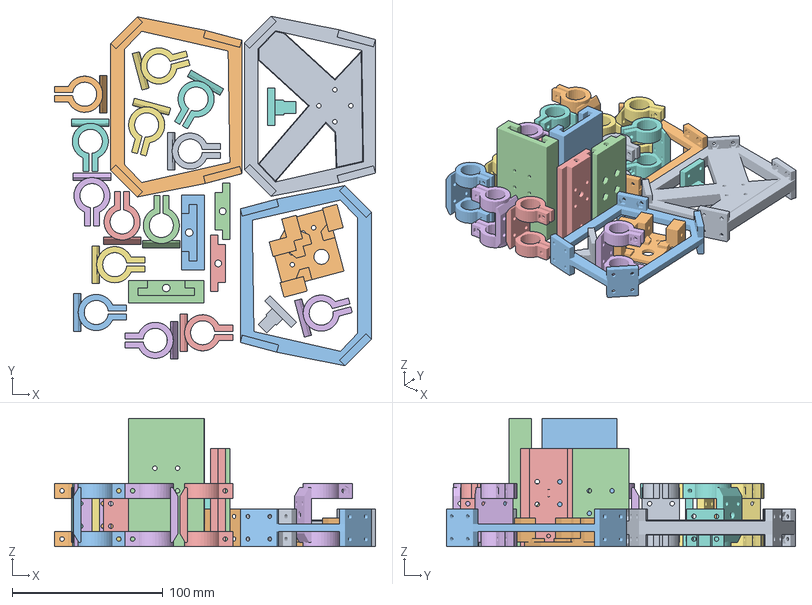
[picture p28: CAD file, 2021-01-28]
cad/output/Whole thing.3mf
213.0 x 231.9 x 85.0 mm
holder_upper.stl
dowel_frame.stl
dowel_frame.stl(1)
rail_inner.stl
rail_inner.stl(1)
clamp_bracket.stl
clamp_bracket.stl(1)
clamp_bracket.stl(2)
clamp_bracket.stl(3)
stage.stl
rail_outer.stl
rail_outer.stl(1)
clamp_bracket.stl(4)
clamp_bracket.stl(5)
clamp_bracket.stl(6)
fixed_stageslide.stl
fixed_stageslide.stl(1)
clamp_bracket.stl(7)
clamp_bracket.stl(8)
clamp_bracket.stl(9)
clamp_bracket.stl(10)
clamp_bracket.stl(11)
clamp_bracket.stl(12)
clamp_bracket.stl(13)

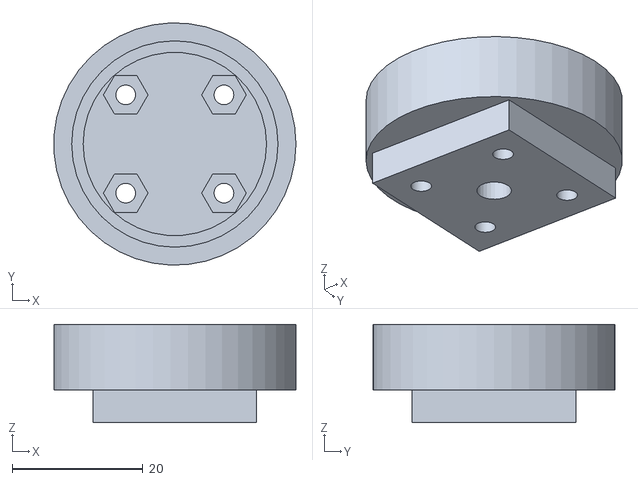
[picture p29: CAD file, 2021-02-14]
cad/output/spkr_holder.stl
37.0 x 37.0 x 15.0

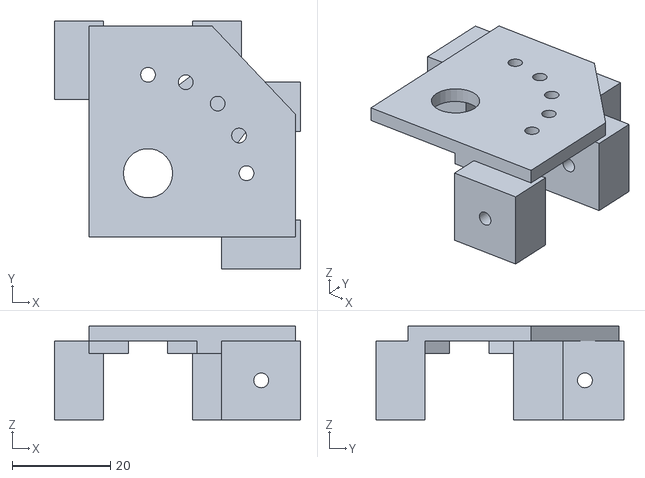
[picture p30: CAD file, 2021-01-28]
cad/output/stage.stl
50.0 x 50.5 x 19.0

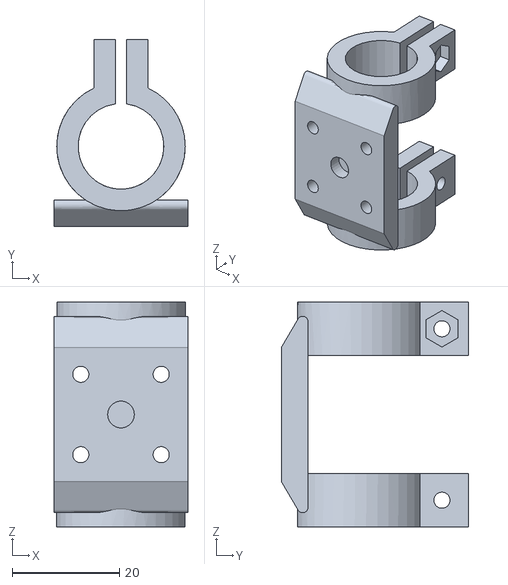
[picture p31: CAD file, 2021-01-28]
cad/output/clamp_bracket.stl
25.0 x 35.0 x 42.0

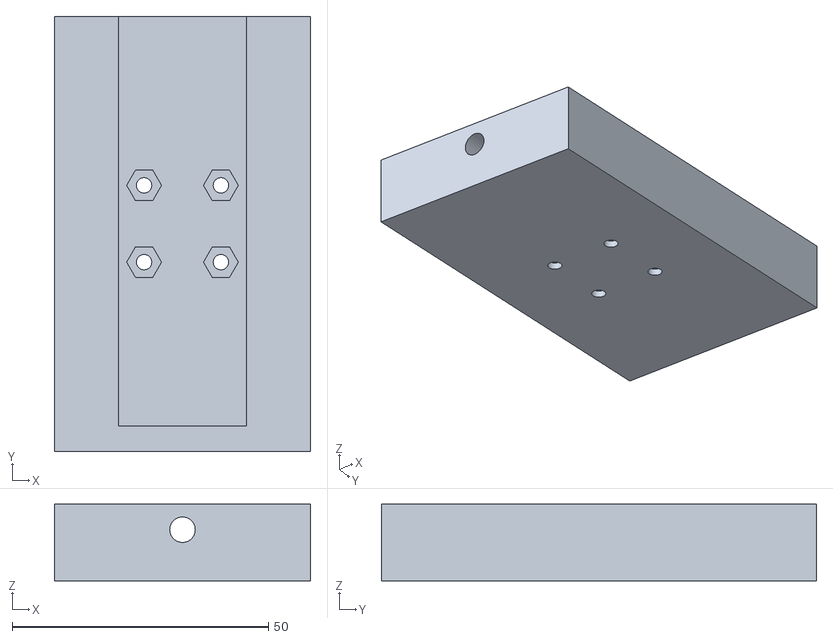
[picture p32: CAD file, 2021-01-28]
cad/output/rail_outer.stl
50.0 x 85.0 x 15.0

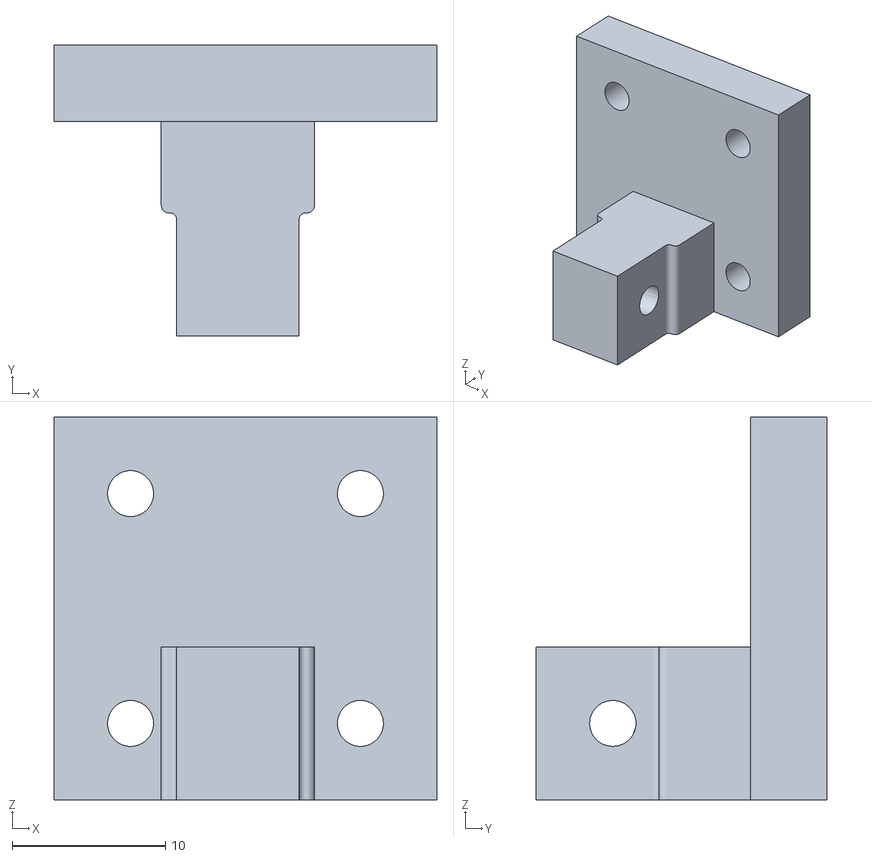
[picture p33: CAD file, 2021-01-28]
cad/output/fixed_stageslide.stl
25.0 x 19.0 x 25.0

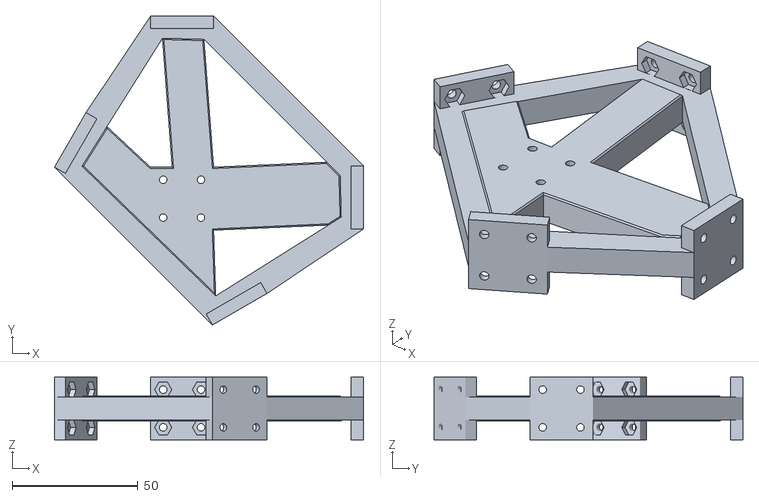
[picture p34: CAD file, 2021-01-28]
cad/output/holder_upper.stl
122.6 x 122.6 x 25.0

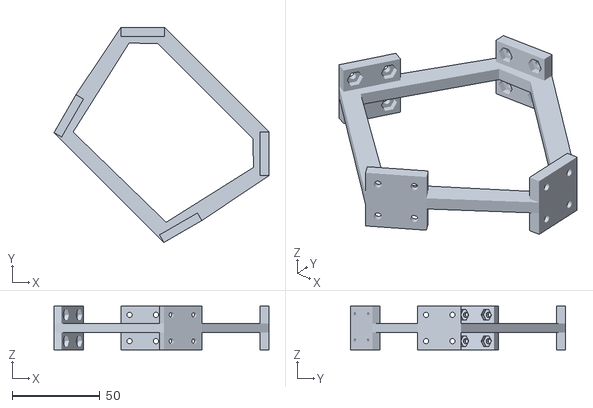
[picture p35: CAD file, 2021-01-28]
cad/output/dowel_frame.stl
122.6 x 122.6 x 25.0

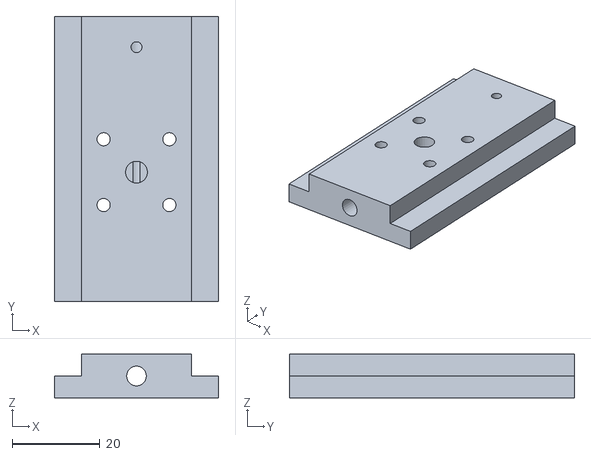
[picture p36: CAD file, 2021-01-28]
cad/output/rail_inner.stl
37.5 x 65.0 x 10.0

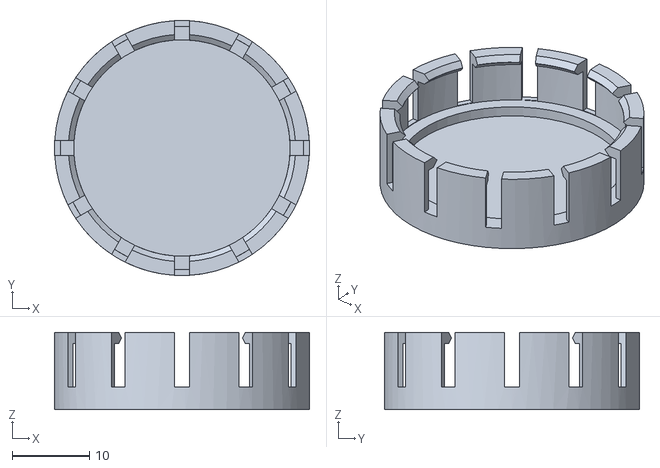
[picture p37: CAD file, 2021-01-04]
cad/output/tabbed_thingy.stl
33.0 x 33.0 x 10.00

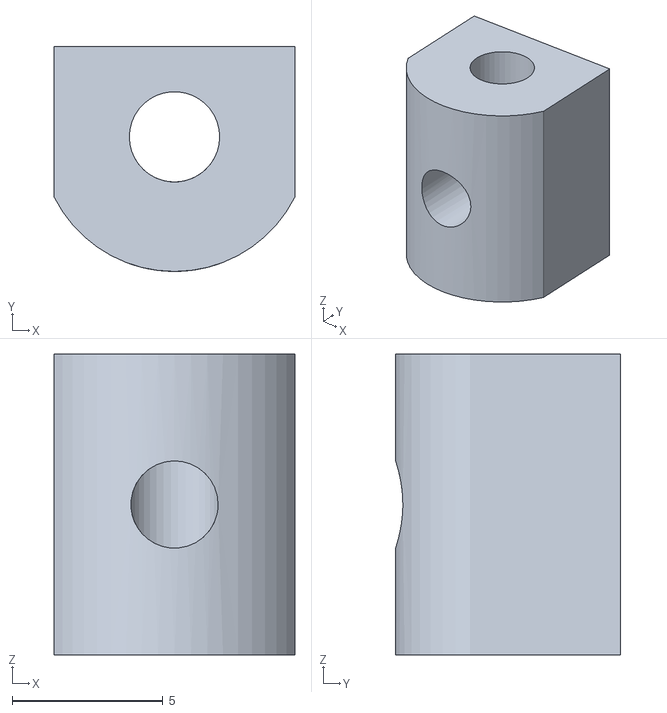
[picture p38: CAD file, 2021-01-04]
cad/output/bracket.stl
8.00 x 7.47 x 10.0

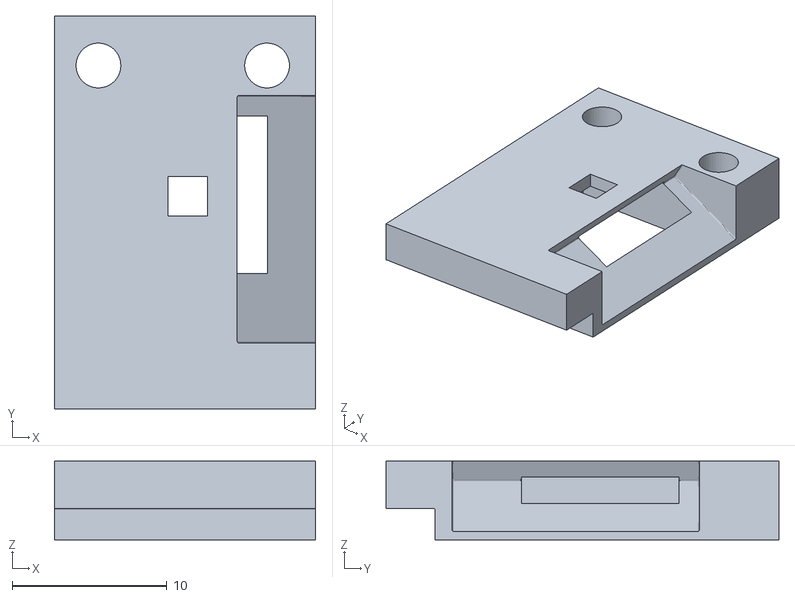
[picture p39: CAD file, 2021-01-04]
cad/output/sensor_cover.stl
16.9 x 25.4 x 5.08

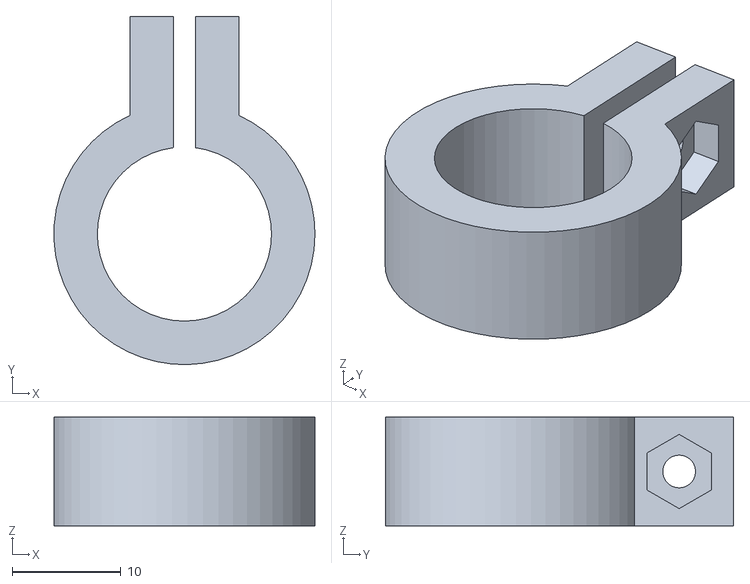
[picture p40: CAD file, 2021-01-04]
cad/output/pipe_clamp_v1.stl
24.0 x 32.0 x 10.0

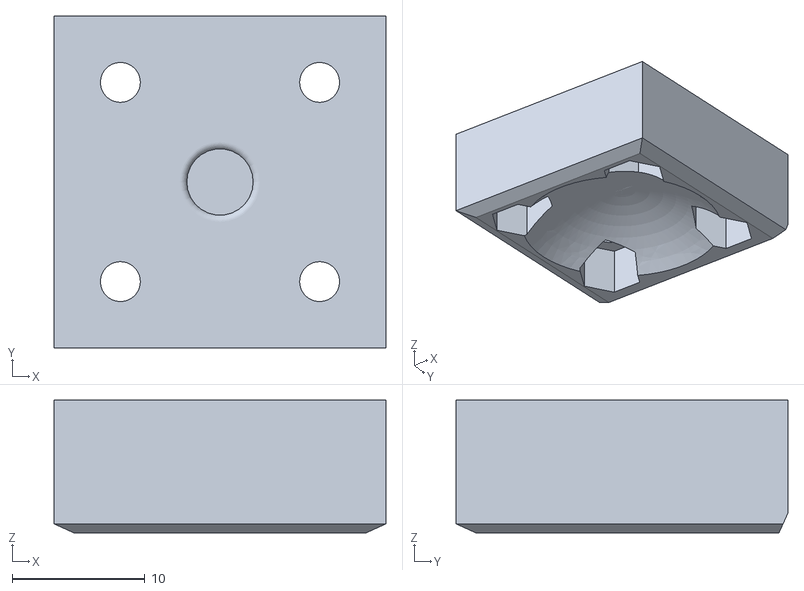
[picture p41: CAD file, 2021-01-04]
cad/output/spkr_bracket.stl
25.0 x 25.0 x 10.0

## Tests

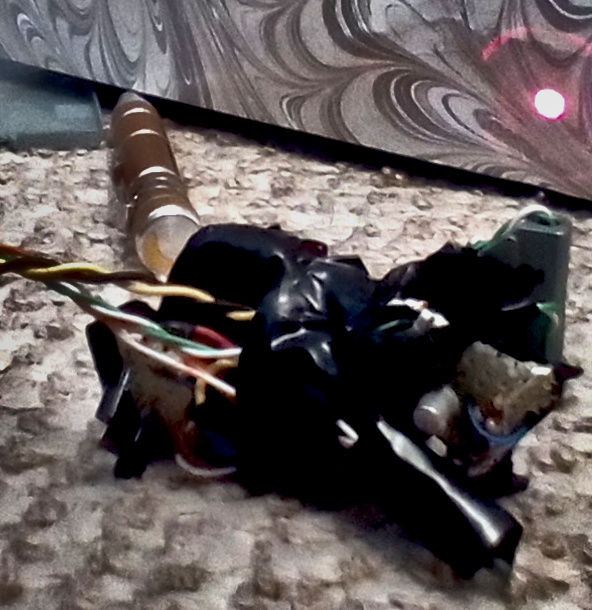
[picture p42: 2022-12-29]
assets/Laser_Driver_V2_test.jpg

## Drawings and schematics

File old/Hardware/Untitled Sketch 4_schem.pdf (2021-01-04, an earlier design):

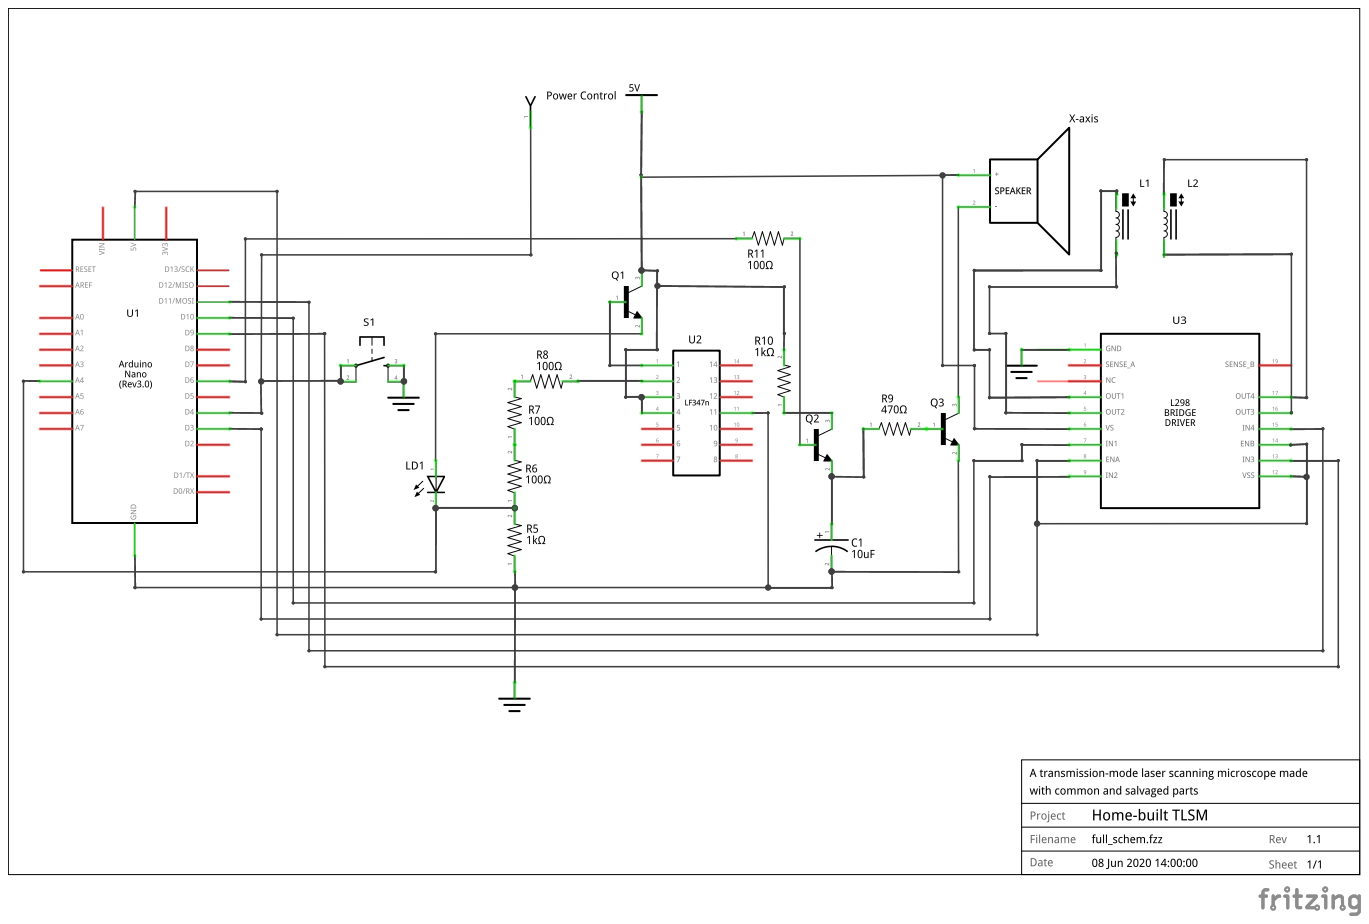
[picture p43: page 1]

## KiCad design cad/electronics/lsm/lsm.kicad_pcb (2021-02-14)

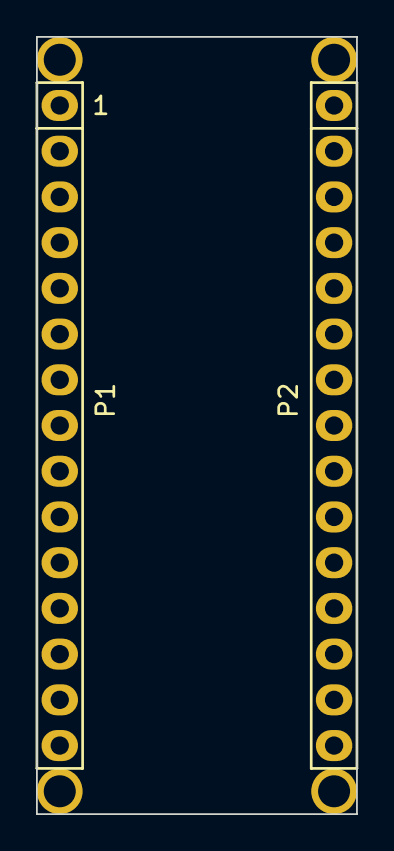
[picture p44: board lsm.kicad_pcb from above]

Board: 2 copper layers, 17.8 x 43.2 mm, 6 parts (0 on the bottom side), 2 nets, no tracks yet.

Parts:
P1: Digital; Socket_Strip_Arduino_1x15
P2: Analog; Socket_Strip_Arduino_1x15
P3, P4, P5, P6: CONN_01X01; 1pin_Nano

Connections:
/Reset: P1.3, P2.3
GND: P1.4, P2.2

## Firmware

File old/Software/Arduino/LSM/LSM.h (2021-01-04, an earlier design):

//LSM.h V1.1.2

/*-----------------*
       LSM.h
  - - - - - - - - -
   This is an easy
   -to-use library
   to control a
   laser and three
   coils set up as
   an LSM.
  -----------------*/

const bool noramp = true; //No ramping. The LSM software can handle that.


//Variables:
int myx = 0; //Current position of specimen
int myy = 0;

//Constants:
//define pin number constants:
const int boardLed = 13; //The Arduino's on-board LED
const int laser = 4; //The pin controling the laser diode
const int coilp1 = 10; //The H-Bridge motor controller inputs:
const int coilp2 = 3;
const int coilp3 = 9;
const int coilp4 = 11;
const int speaker = 6; // PWM pin for speaker control
const int ldr0 = 0; //The Photoresistor voltage divider circuits
const int ldr1 = 1;
const int thumbX = 2;
const int thumbY = 3;
const int currentsense = 4;

//True and False (For those who do python):
const bool True = false;
const bool False = true;

//define functions:
void initLSM(void);
void setlaser(bool state);
void setLed(bool state);
void place(int x, int y);
void rampPWM(int pin, int current, int target, int rate);
int getLDR(int pin);
int getThumbStick(int axis);
int getx(void);
int gety(void);


int getx(void){
  return myx;
}
int gety(void){
  return myy;
}

void initLSM(void) {
  pinMode(boardLed, OUTPUT);
  pinMode(laser, OUTPUT);
  pinMode(coilp1, OUTPUT);
  pinMode(coilp2, OUTPUT);
  pinMode(coilp3, OUTPUT);
  pinMode(coilp4, OUTPUT);
  digitalWrite(laser, 1); //High is false. Defaults to on.
}

void setLaser(bool state) { //Set Laser State
  digitalWrite(laser, not state);
}

void setLed(bool state) { //Set Laser State
  digitalWrite(boardLed, state);
}

void rampPWM(int pin, int current, int target, int rate) { //low-level function to simply bring an axis to its position slowly, as to increase the lifespan of the CD read/write head
  while (abs(current - target) > (rate * 2)) {
    delay((10 / rate));
    if (current > target) {
      current = current - rate;
    }
    else {
      current = current + rate;
    }
    analogWrite(pin, current);
  }
  analogWrite(pin, target); //If it is a few off, we bring it back over
}

void place(int x, int y) {
 if((abs(myx-x)<10) || noramp){ //No ramping, just setpos
   if (x >= 0) {
     myx = x;
     analogWrite(coilp2, 0);
     analogWrite(coilp1, (x)); //PWM
   }
   else {
     myx = x;
     analogWrite(coilp1, 0);
     analogWrite(coilp2, abs(x)); //PWM in the other direction
   }
 }
 else {
    if (x >= 60) {
     rampPWM(coilp2, myx, 0, 4);
     rampPWM(coilp1, myx, x, 4);
     myx = x;
     analogWrite(coilp2, 0);
     analogWrite(coilp1, (x)); //PWM
   }
   else { //A little ways away, let's ramp it.
     rampPWM(coilp1, myx, 0, 4);
     rampPWM(coilp2, myx, x, 4);
     myx = x;
     analogWrite(coilp1, 0);
     analogWrite(coilp2, abs(x)); //PWM in the other direction
   }
 }
 if((abs(myy-y)<60) || noramp){ //No ramping, just setpos
   if (y >= 0) {
     myy = y;
     analogWrite(coilp4, 0);
     analogWrite(coilp3, y); //PWM
   }
   else {
     myy = y;
     analogWrite(coilp3, 0);
     analogWrite(coilp4, abs(y)); //PWM in the other direction
   }
 }
 else {
    if (y >= 0) {
     rampPWM(coilp4, myy, 0, 4);
     rampPWM(coilp3, myy, y, 4);
     myy = y;
     analogWrite(coilp4, 0);
     analogWrite(coilp3, (y)); //PWM
   }
   else { //A little ways away, let's ramp it.
     rampPWM(coilp3, myy, 0, 4);
     rampPWM(coilp4, myy, abs(y), 4);
     myy = y;
     analogWrite(coilp3, 0);
     analogWrite(coilp4, abs(y)); //PWM in the other direction
   }
 }

}
int getLDR(int pin) {
  return analogRead(pin);
}

void setspeaker(int val) {
  analogWrite(speaker, val);
}

int getThumbStick(int axis) {
  return analogRead(axis);
}

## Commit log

2021-01-04 Initial commit (before my hard drive fails)
    [Laser_Driver.fzz, PWM_averager.fzz, Writing_Project_Tracker.ods, bracket.stl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]
2021-01-09 Fixed stage stuff.
2021-01-17 Pretty much finished an xy-mount for the opu. Two rails!
2021-01-18 Redesigned clamps & repositioned dowels accordingly.
2021-01-21 added frame models
2021-01-23 Fixed frame pieces & made X/Y rail attatchment pieces
2021-01-28 Got UDP communication between Java and C++ on the ESP8266
    [Whole thing.3mf, clamp_bracket.stl, dowel_frame.stl, fixed_stageslide.stl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]
2021-02-14 Started KiCad schematics and improved code.
    [lsm.kicad_pcb, lsm.sch]
2021-02-14 Almost finished with schematic.
    [lsm.sch]
2021-02-14 Fixed the speaker holder. It should now print nicely.
    [spkr_holder.stl]
2022-12-29 some cleanup
    [1eaf60ad-HEAD.csv]
